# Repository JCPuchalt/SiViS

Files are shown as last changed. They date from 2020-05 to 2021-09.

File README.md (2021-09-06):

# SiViS
New methods for C. elegans assays lifespan automation have been evaluated, these are for improving C. elegans deteccion, and these are described in research article [1].
In addition, other methods are used for vision system inspection [2] and for c-elegans detection [3], all of these are evaluated.

### Research article [1]
[1] Puchalt JC, Sánchez-Salmerón AJ, Ivorra E, Llopis S, Martínez R, Martorell P. Small flexible automated system for monitoring Caenorhabditis elegans lifespan based on active vision and image processing techniques. Sci Rep. 2021 Jun 10;11(1):12289. doi: 10.1038/s41598-021-91898-6. PMID: 34112931; PMCID: PMC8192789.

### Research article [2]
[2] Puchalt JC, Sánchez-Salmerón AJ, Martorell Guerola P, Genovés Martínez S (2019) Active backlight for automating visual monitoring: An analysis of a lighting control technique for Caenorhabditis elegans cultured on standard Petri plates. PLOS ONE 14(4): e0215548. https://doi.org/10.1371/journal.pone.0215548

### Research article [3]
[3] Puchalt, J.C., Sánchez-Salmerón, A., Ivorra, E. et al. Improving lifespan automation for Caenorhabditis elegans by using image processing and a post-processing adaptive data filter. Sci Rep 10, 8729 (2020). https://doi.org/10.1038/s41598-020-65619-4

#### Example assemby and code on [2]
* It is described in document https://github.com/JCPuchalt/c-elegans_smartLight

#### Example code on [3]
* It is described in document https://github.com/AntonioJoseSanchezSalmeron/lifespan

#### Hardware description on [1]
In this repository are the .stl files to print in 3D printer. 
* bridge.stl
* door.stl
* filter.stl
* lid.stl
* pre_rack.stl
* rack.stl
* electronicBox.stl
* displayBox.stl
* frame.stl
* bolt.stl

Then assemby vibration system and adjust to vision system as follow 
https://github.com/JCPuchalt/SiViS/blob/master/AssemblyManual.pdf

#### Pallet assembly
These are the parts:
* pallet_rigidPart.stl
* pallet_middlePart.stl
* pallet_flexiblePart.stl

Assembly the pallet part as follow https://github.com/JCPuchalt/SiViS/blob/master/AssemblyPallet.pdf

## The Code
You shall download this repository on Ubuntu 18.04 machine in the folder you wish. 
Once download, open a terminal and set in the SiViS folder.
1. CaptureCE_App:
   Then follow the README.md file of Code/CaptureCE_App folder.
2. ProcessorCE_App:
   Then follow the README.md file of Code/ProcessorCE_App folder.
3. SiViS_App:
   Then follow the README.md file of Code/SiViS_App folder.

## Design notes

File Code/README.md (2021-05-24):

## The code
There are three pieces of software.

* SiViS_App (Running on Raspberry Pi)
* CaptureCE_App (Running on Desktop Computer)
* ProcessorCE_App (Running on Desktop Computer)

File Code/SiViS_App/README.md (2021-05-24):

## SiViS_App
This code is downloaded and installed on Rasperry Pi 4. 
It may be useful to consult previous documentation in https://github.com/JCPuchalt/c-elegans_smartLight.

### Hardware description
Components:
* Raspberry Pi 4
* Pi NoIR Camera V1
* 7" Raspberry Pi Display
* Raspberry power supply (at least 2Amp)
* Micro SD card (at least 16GB)

The camera should be coplanar to the display focusing at the center of it at a distance of about 8cm.
The camera and the display must be firmly grasped, since any minimum displacement will decalibrate 
the camera-display correspondences.

### Easy software installation
* Install raspbian on Raspberry Pi 4. 
    1. Download raspbian installer (NOOBS) from https://www.raspberrypi.org/downloads/noobs/
    2. Unzip the downloaded files
    3. Format a Micro SD with FAT32
    4. Copy the unzipped files into the formatted Micro SD.
    5. Place Micro SD into Micro SD card slot of Raspberry Pi.
    6. Connect to Ethernet.
    7. Connect power supply and follow the raspbian installation instructions indicated on display.
    8. Write down the Raspberry Pi IP address. To find it, on a terminal type: 
        `ifconfig` 
* From Raspberry Pi open a Terminal. 
    1. Copy the SiViS\_App folder into (i.e.) [/home/pi].       
    2. Launch file set\_up\_whole\_system.sh and follow instructions. On terminal, set file folder (for example: /home/pi/SiViS\_App) 
        ````
        cd /home/pi/SiViS_App
        chmod +x set_up_whole_system.sh
        sh ./set_up_whole_system.sh
        ````

## Software installation details of set_up_whole_system.sh. It will install and set:

* Download and install OpenCV 3.0 and opencv_contrib
* Download and install userland in [/home/pi/userland] 
(https://github.com/raspberrypi/userland)
* Set GPU memory at 256MB
* Temporarily increase the swap
* Free some memory
* Install libncurses5-dev libncursesw5-dev
* Install git
* Enable SSH
* Enable camera
* Disable camera led
* Download and install SiViS\_App program. Copy code in a folder [/home/pi/]
    ````
    cd SiViS_App
    cmake .
    make
    ````

## Run code on Raspberry Pi
Connect from PC to Raspberry Pi through SSH (on Windows with PuTTY (https://www.ssh.com/ssh/putty/download) or Linux with terminal `ssh pi@Raspberry_IP_Adrees`). That terminal is connected to Raspberry, so type on that terminal:
````
cd SiViS_App
sudo ./c-elegans
````

## Notes

* Make sure that the calibration pattern is captured completely with the camera.
To move it you can modify it with the file "./calibracio/p1.xml".

* Some libraries such as WiringPi may be required for compilation, but they are not required for the application

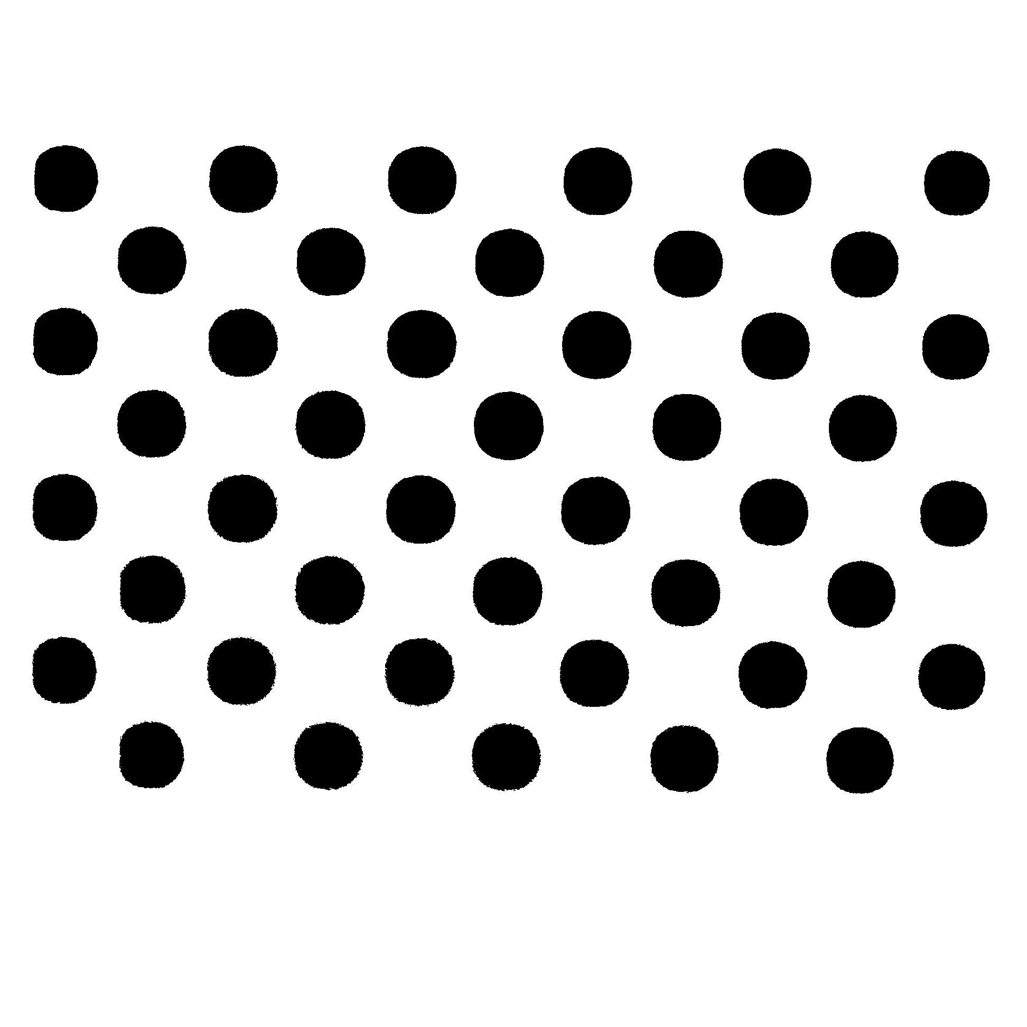
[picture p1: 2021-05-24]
Code/SiViS_App/Patern21.bmp

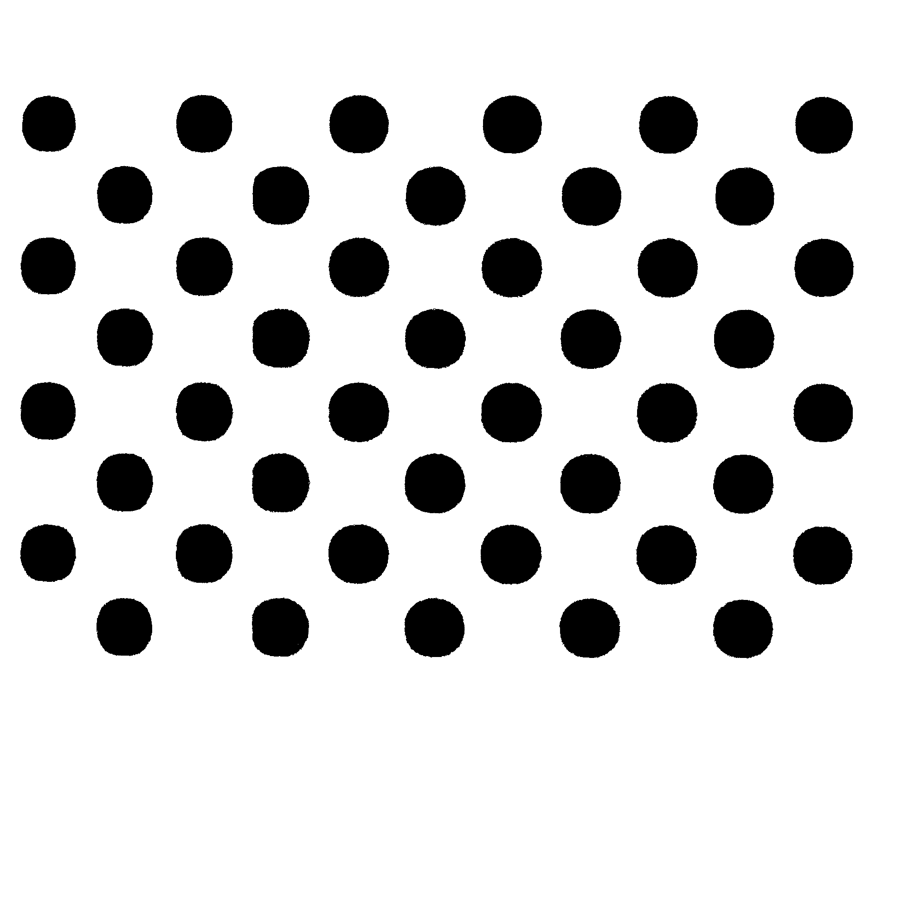
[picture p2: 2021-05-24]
Code/SiViS_App/Patern11.bmp

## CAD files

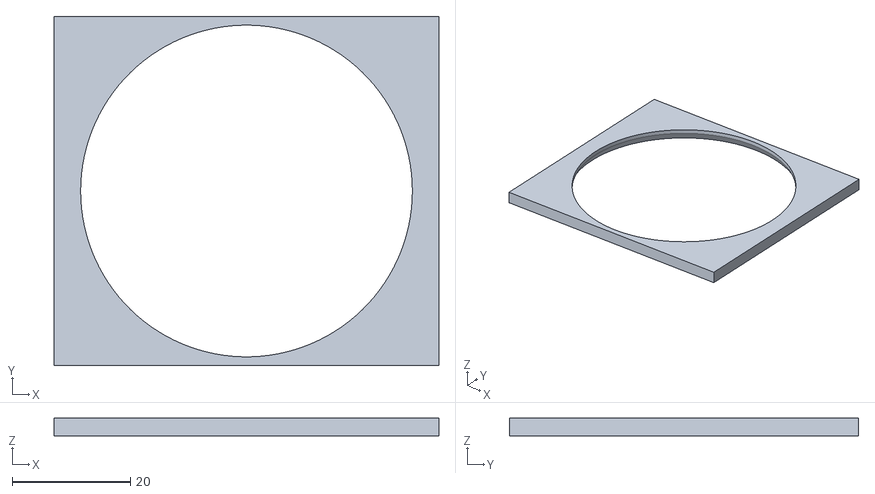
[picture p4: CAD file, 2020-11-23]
Pallet assembly/pallet_flexiblePart.stl
65.0 x 59.0 x 3.00

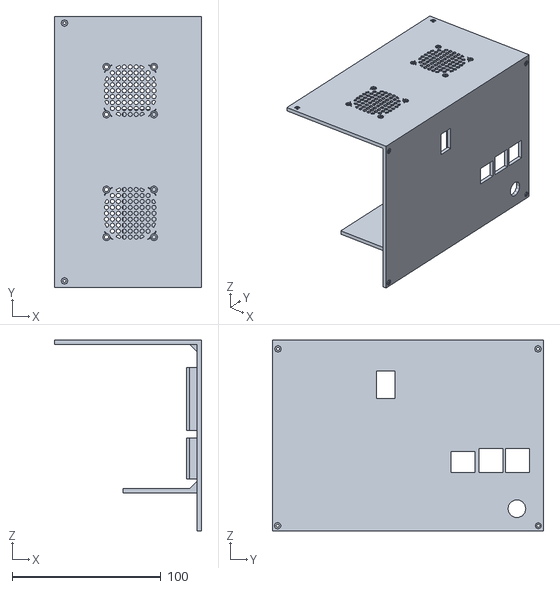
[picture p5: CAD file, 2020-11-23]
assembly parts/lid.stl
99.0 x 182.6 x 128.6

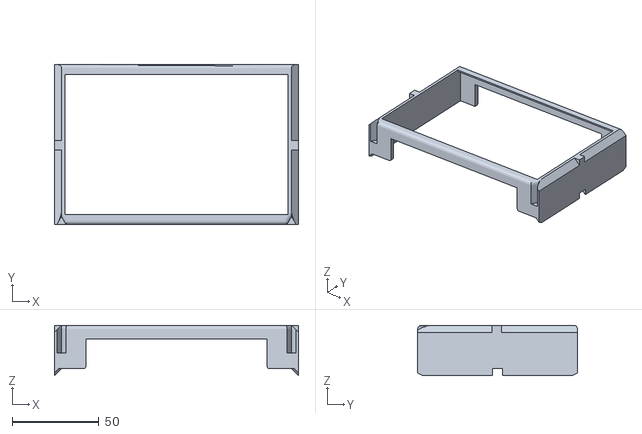
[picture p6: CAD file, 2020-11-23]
Pallet assembly/pallet_rigidPart.stl
140.5 x 92.0 x 29.0

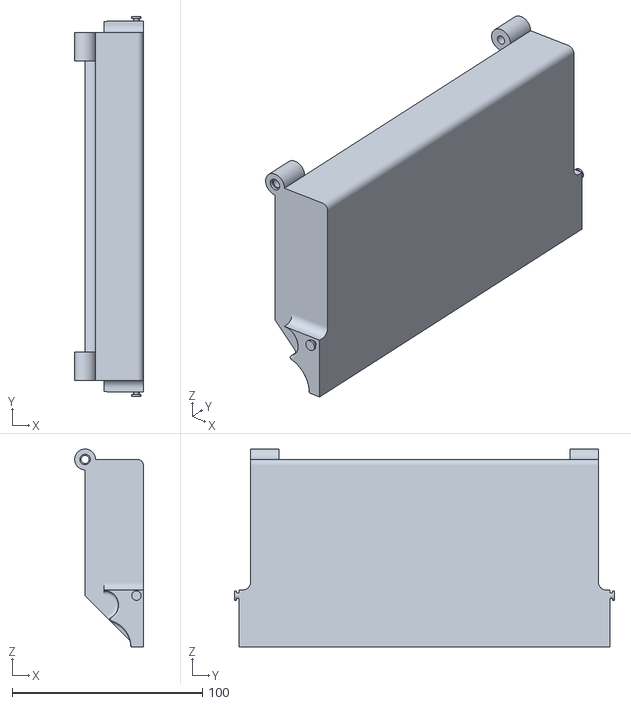
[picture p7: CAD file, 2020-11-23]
assembly parts/door.stl
36.1 x 199.9 x 104.1

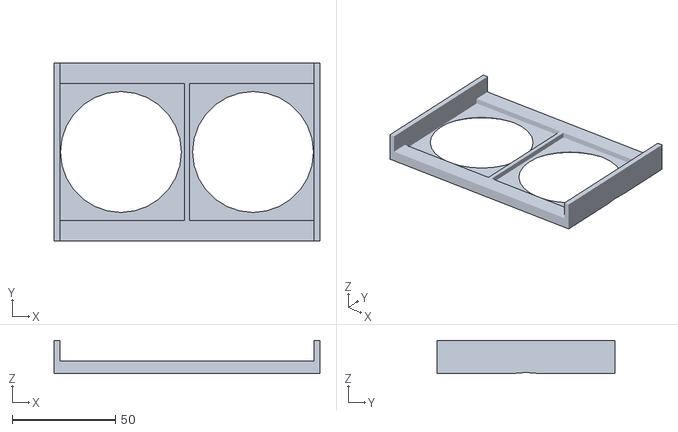
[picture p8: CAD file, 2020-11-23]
Pallet assembly/pallet_middlePart.stl
128.7 x 86.0 x 16.0

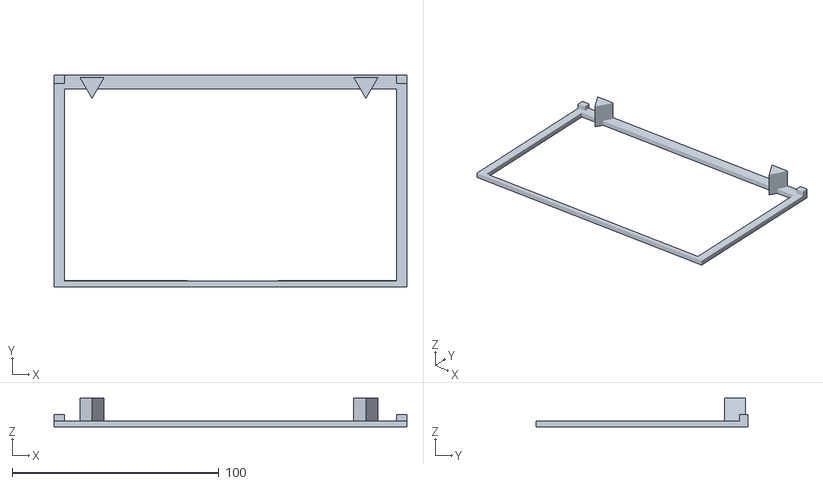
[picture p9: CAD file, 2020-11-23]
assembly parts/frame.stl
170.8 x 102.5 x 14.0

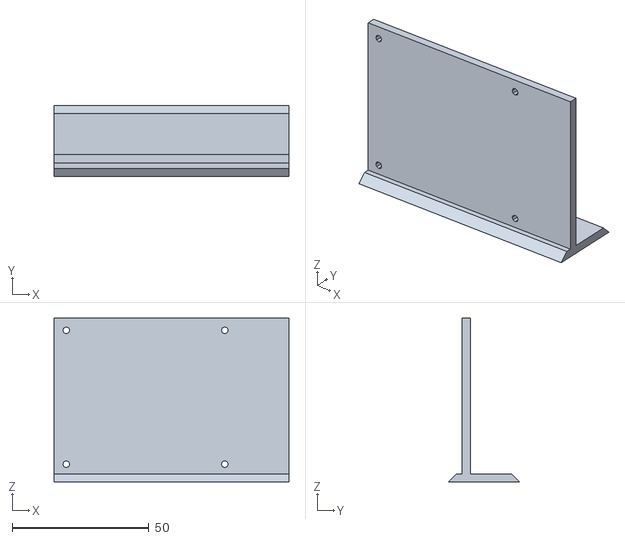
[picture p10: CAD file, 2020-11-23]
assembly parts/rack.stl
86.0 x 26.0 x 60.0

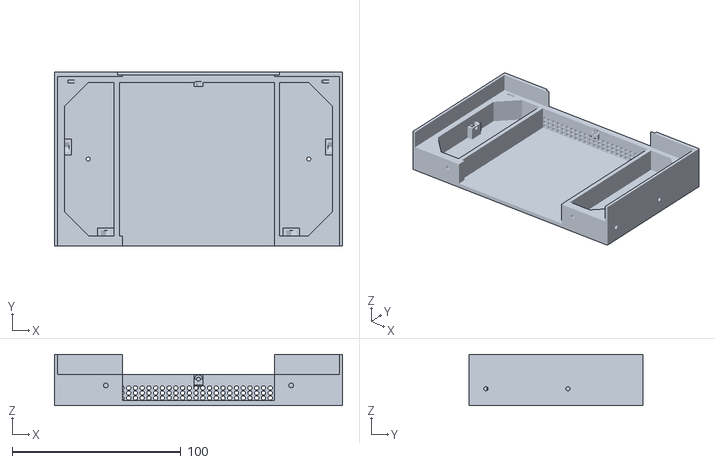
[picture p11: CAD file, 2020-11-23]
assembly parts/displayBox.stl
170.9 x 103.1 x 30.4

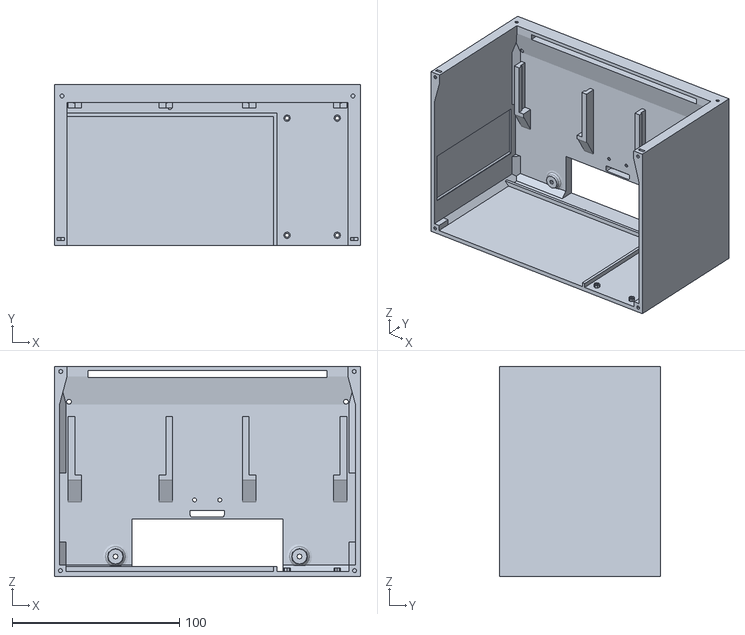
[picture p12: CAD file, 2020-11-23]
assembly parts/electronicBox.stl
182.9 x 96.0 x 125.6

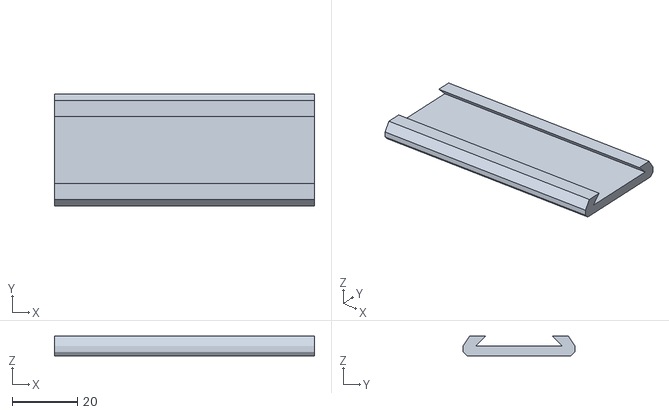
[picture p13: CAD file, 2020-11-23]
assembly parts/pre_rack.stl
80.0 x 34.5 x 6.00

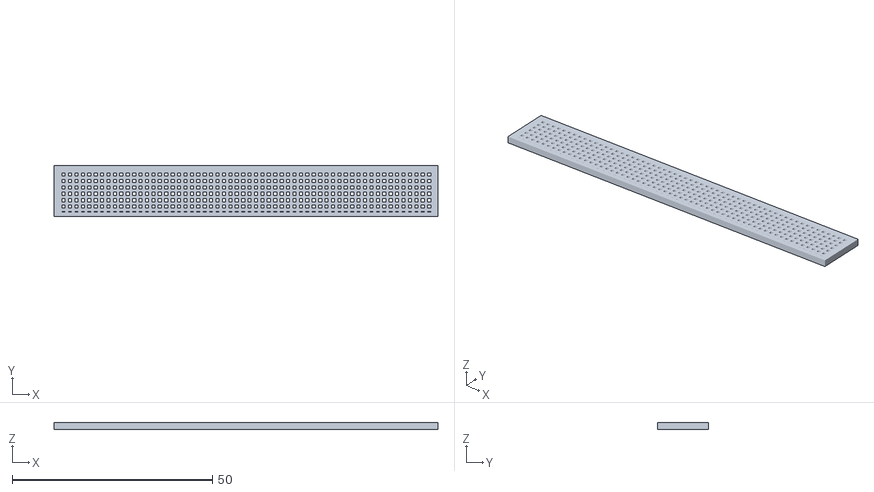
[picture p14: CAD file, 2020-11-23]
assembly parts/filter.stl
95.8 x 12.8 x 1.70

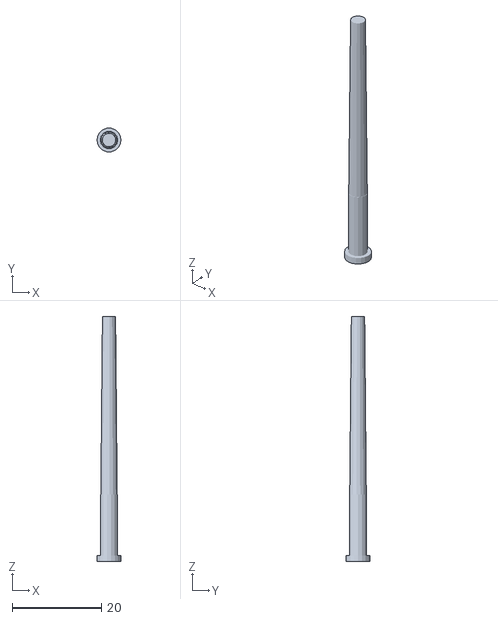
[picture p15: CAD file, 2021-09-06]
assembly parts/bolt.stl
5.40 x 5.32 x 55.0

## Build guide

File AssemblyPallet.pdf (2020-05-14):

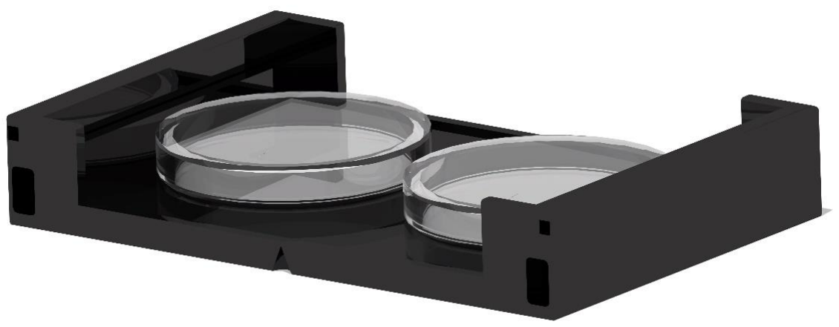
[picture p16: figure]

Joan Carles Puchalt · Antonio Sánchez · Eugenio Iborra · Roberto Martínez · Salvador Genovés · Patricia Martorell

### 1 SiViS assemby manual

# SiViS

## Prototype V1.1

# ASSEMBLY MANUAL

# Pallet

### These are the parts:

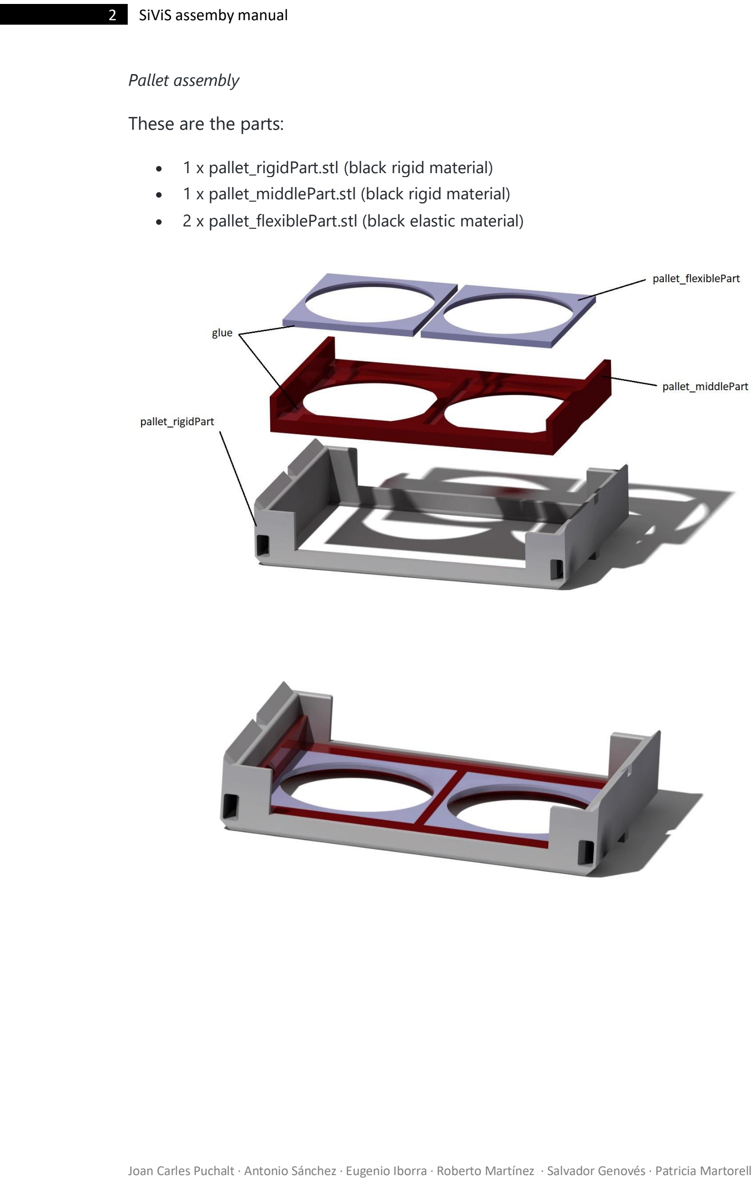
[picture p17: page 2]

Joan Carles Puchalt · Antonio Sánchez · Eugenio Iborra · Roberto Martínez · Salvador Genovés · Patricia Martorell

### 2 SiViS assemby manual

Pallet assembly

- 1 x pallet_rigidPart.stl (black rigid material)
- 1 x pallet_middlePart.stl (black rigid material)
- 2 x pallet_flexiblePart.stl (black elastic material)

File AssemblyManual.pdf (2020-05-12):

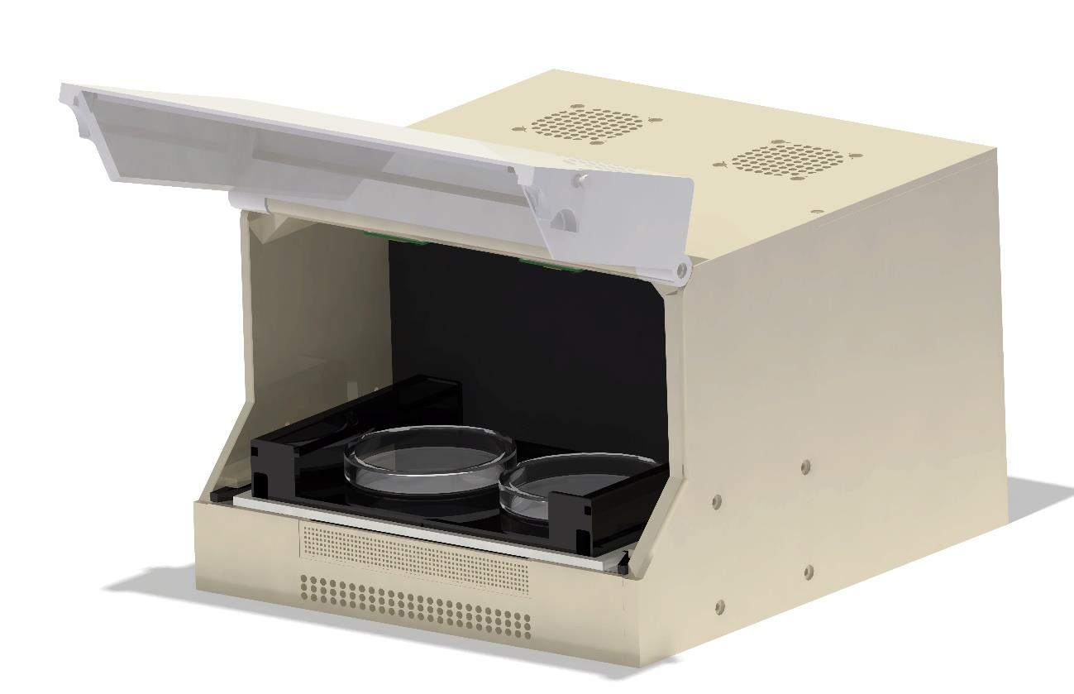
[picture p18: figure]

Joan Carles Puchalt · Antonio Sánchez · Eugenio Iborra · Roberto Martínez · Salvador Genovés · Patricia Martorell

1 SiViS assemby manual

# SiViS

## Prototype V1.1

# ASSEMBLY MANUAL

# PROTOTYPE V1.1

INTRODUCTION

This manual purpose is to help the successfully SiViS assembly, that is, a device created to capture images of C. elegans in a controlled environment.

At first, we (the authors) are going to supply a list of components, describing precisely each component with the aid of figures. Besides, we are going to include also the material features for every component, and an assembly diagram. The parts are jointed together with bolts and screws and, in some cases, glue.

COMPONENT LIST

The component list needed in order to assemble this device is the following:

- Bridge (x1) – Plastic PLA (Polylactic Acid)
- Door (x1) – Plastic PLA (Polylactic Acid)
- Filter (x1) – Plastic PLA (Polylactic Acid)
- Lid (x1) – Plastic PLA (Polylactic Acid)
- Pre-rack (x1) – Plastic PLA (Polylactic Acid)
- Rack (x1) – Plastic PLA (Polylactic Acid)
- Electronic box (x1) – Plastic PLA (Polylactic Acid)
- Display Box (x1) – Plastic PLA (Polylactic Acid)
- Frame (x1) – Plastic PLA (Polylactic Acid)

We employ bolts, screws and glue to assemble, so we provide the following list:

- Plastic bolts (2 units). PLA printed
- Screw M2x12 (8 units). Steel
- Screw M2x10 (6 units). Steel
- Screw M2.5x30 (2units). Steel
- Screw M2.5x20 (6 units). Steel
- Screw M3x30 (4 units). Steel
- Glue (silicone-based)

We too need the electronics parts, which are the following:

- 1 Camera Multiplexer IVPORT Rev.3
- 1 Flat Ribbon Cable 10 cm (FRC100)
- 3 Flat Ribbon Cable 20 cm (FRC200)
- 2 Camera Raspberry Pi
- 1 Raspberry Pi 7” display

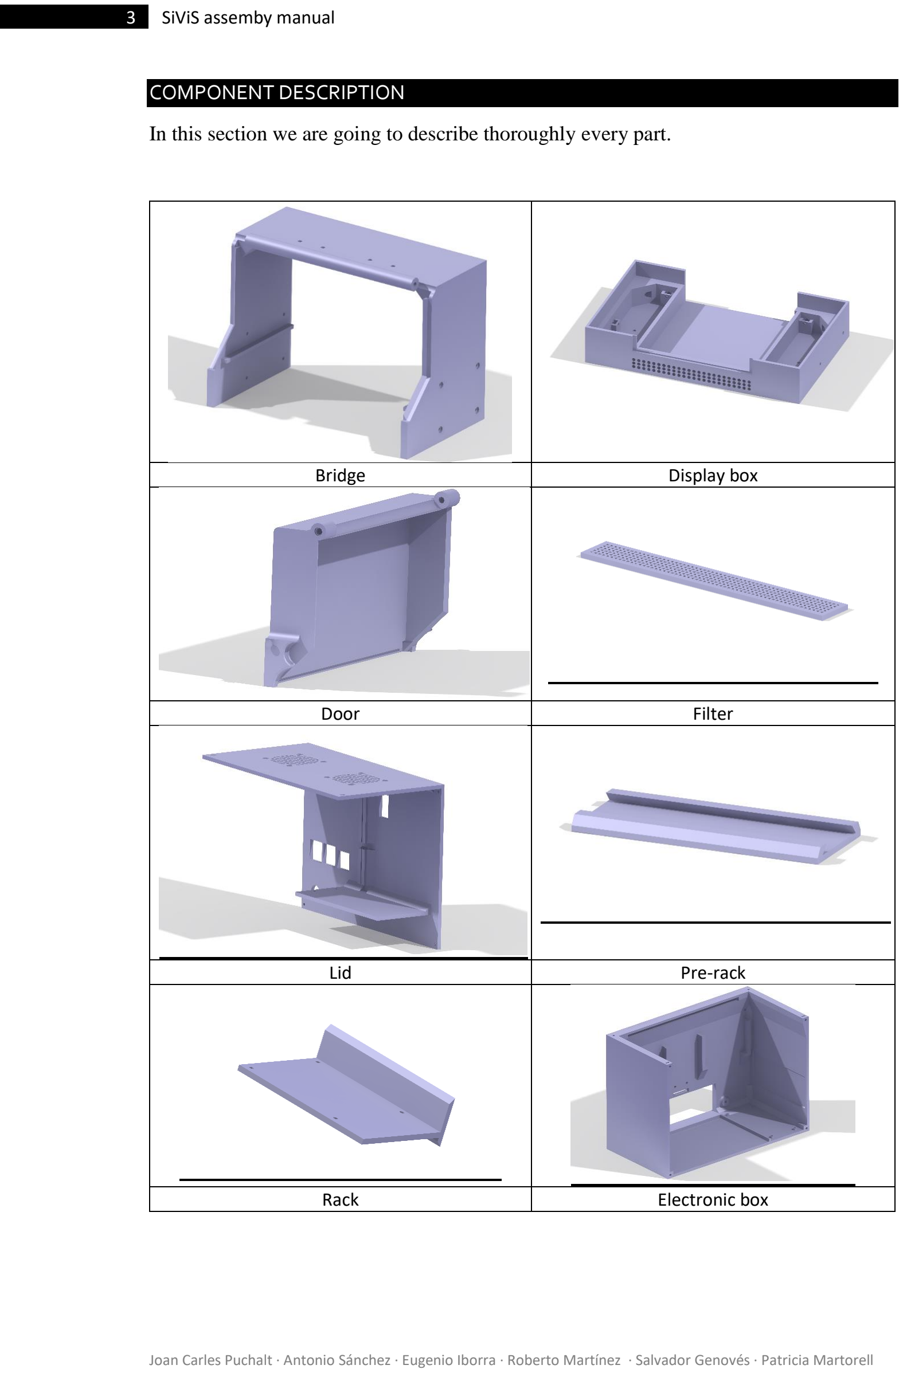
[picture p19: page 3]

COMPONENT DESCRIPTION

In this section we are going to describe thoroughly every part.

Bridge | Display box
Door | Filter
Lid | Pre-rack
Rack | Electronic box

Bridge:

This piece is enough rigid to avoid deformations, where the two cameras are fixed on the top. The door is fixed in the bridge axis with two bolts. On the bottom ‘display box’ is placed.

Display box:

Into this box is placed the display (lighting system), it has holes to allow air flowing. In this piece, the ‘Filter’ is pasted with glue in the slot to avoid dirt.

Door:

This piece purpose is to allow the expert to replace the Petri plates, while avoiding that the plates will be exposed to external light.

Filter:

This is a small part; its purpose is to filter the external air to avoid dust pollution of the plates while these are inside the device and let in air to refrigerate the display.

Lid:

This piece protects the electronic parts of the device from external dust and strikes. This part has two hole patterns in one of its sides, where we need to fasten two fans in order to force air flowing to dissipate the heat generate by the electronic components. It has wireways printed on lid.

Pre-rack:

This is a piece that is glued to the wall of the ‘Electronic box’. It is a prismatic piece, with a dovetail to assemble with the rack (the rack fixes the Raspberry Pi).

Rack:

This piece is where we install a Raspberry Pi.

Electronic box:

This is the piece that we fasten to the back of the bridge piece, where all the electronics are installed. The tree parts (display box, bridge and electronic box) have pipes between them to allow crossing the air flow.

Frame:

This part is to hold the pallet, where Petri plates are placed, thus Petri plates are always at the same position.

UNION METHODS

Here we provide a list of the needed screws to mount the device:

- Plastic bolts (2 units).PLA
- Screw M2x12 (8 units). Steel
- Screw M2x10 (6 units). Steel
- Screw M2.5x30 (2units). Steel
- Screw M2.5x20 (6 units). Steel
- Screw M3x30 (4 units). Steel
- Glue (silicone-based)

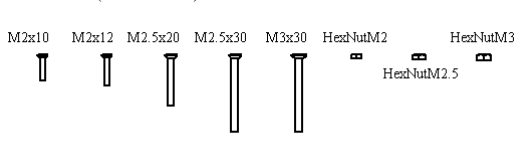
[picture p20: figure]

Plastic bolts:
These bolts are made of Polylactic Acid plastic. We made them via additive

ELECTRONICS COMPONENTS

In this section we describe the electronic components needed in order to the SIVIS device to work properly. The list is the following:

Camera Multiplexer IVPORT Rev.3:

This electronic part’s function is to connect the Flat Ribbon Cable to multiplex the signal received from the camera’s controller (A raspberry Pi). It is a red PBC with four outputs and one input. Here is a photo of this PCB:

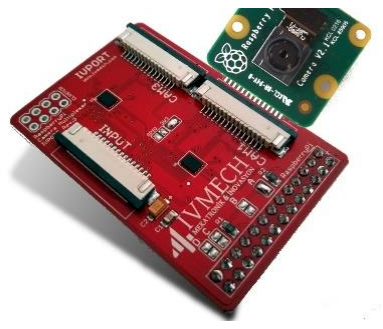
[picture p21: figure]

Multiplexer

Flat Ribbon Cable 10 cm and 20 cm:

It is printed circuitry in a flexible plastic matrix to transfer data between electronic devices.

Camera Raspberry Pi:

That camera is fastened to the ‘Bridge’ piece, where it goes on the inside ceiling of that piece. It is really a little PCB with a mini camera welded on top with tin wire.

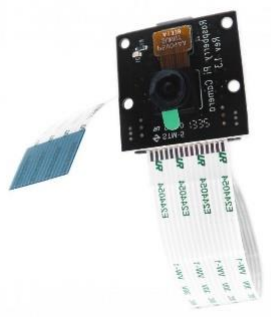
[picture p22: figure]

The Raspberry Pi Camera

We need two units of that electronic device. These are fastened to the inside ceiling of the ‘Bridge’ piece with screws.

ASSEMBLY SCHEME

## Preparing the pieces:

1. Remove excess material from each plastic component carefully.
2. Paste the filter on the front side of the display box.
3. Paste the rubber vibrator on the frame vibrator.
4. Place and paste the pre-rack on one side of the electronic box.
5. Place the nuts in its places (nut holes) and fix with glue. Be careful not to occlude the inner part of the hole.
a. Metric 2mm nuts.
b. Metric 2.5mm nuts.
c. Metric 3mm nuts.
6. Cut the EVA rubber, cover and paste to the inspection inner.
7. Remove touchscreen from display. Touchscreen is fixed with thermal glue, which to weaken it must be heated to 70 degrees during five minutes.
8. Connect the driver to the display.
9. Install the wiring in the ‘Lid’ piece.
a. Place the fans and screw to the lid.
b. Place the switch in the lid.
c. Place the power connector.
d. Follow the electric scheme.

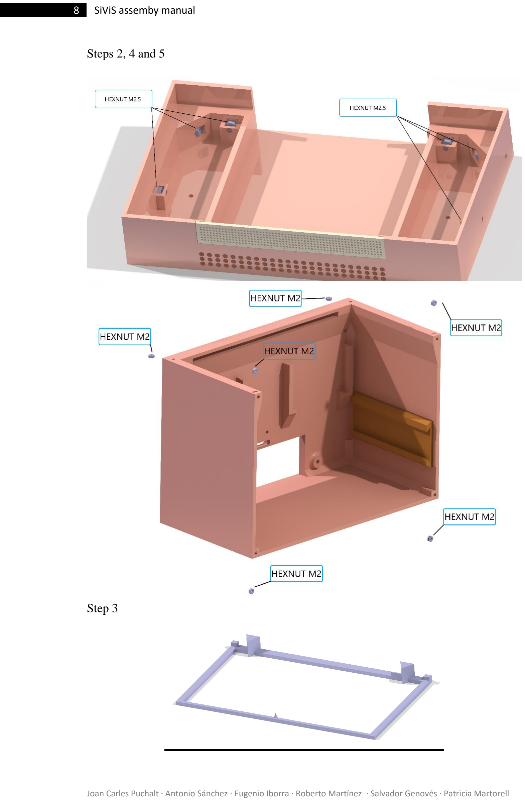
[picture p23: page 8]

Steps 2, 4 and 5

Step 3

## Assembly:

10. Place the cameras in its position and screw them to the ‘Bridge’ piece.
11. Place the display in the display box and place the diffuser on display.
12. Place the frame vibrator on the diffuser.
13. Screw the bridge and the display box between them.
14. Pass the camera cables and the display cable through the slots to electronic box
15. Screw the electronic box to the bridge and to the display box.
16. Screw the Raspberry Pi to the rack and place the rack in the pre-rack slot.
17. Connect the cables.
a. Connect the camera cables to the multiplexer.
b. Connect the input multiplexer to the camera slot in Raspberry Pi.
c. Connect the Dupont cable of multiplexor to GPIO.
d. Connect the display cable to the camera slot of Raspberry Pi.
e. Connect the Dupont cable of display supply to the Raspberry Pi GPIO.
f. Connect the Dupont cable supply to the Raspberry GPIO.
18. Place the lid and screw it to the electronic box.
19. Place the door and introduce the two bolts in their holes.

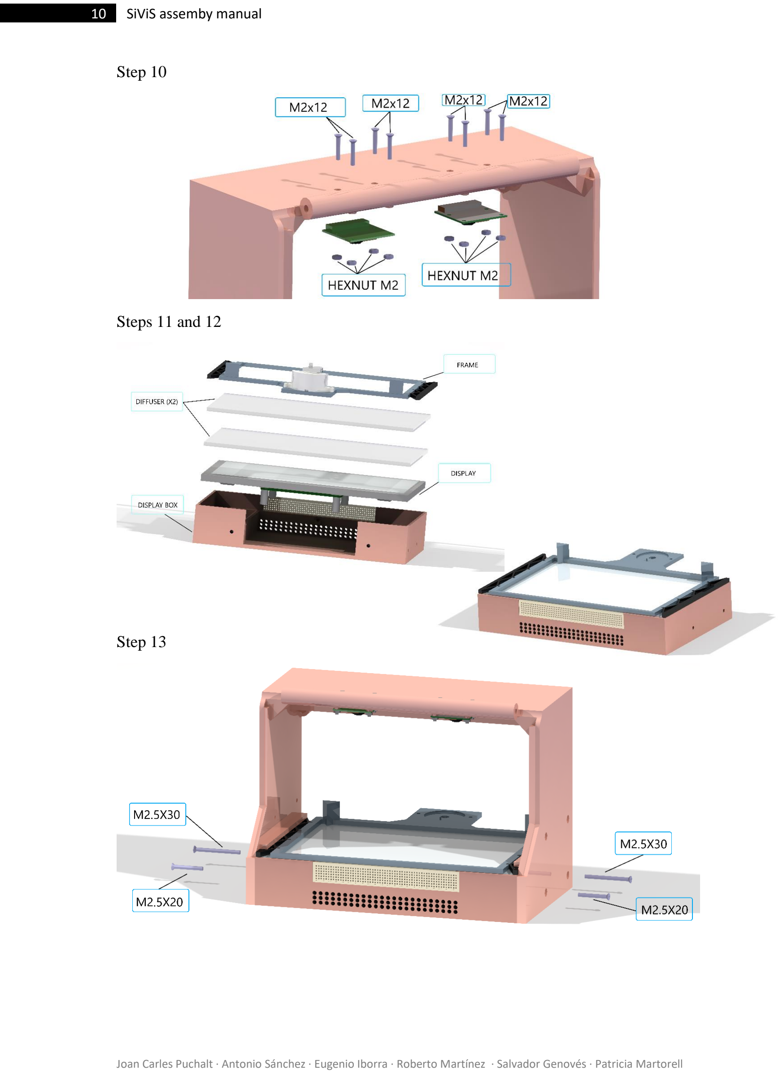
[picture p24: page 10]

Step 10

Steps 11 and 12

Step 13

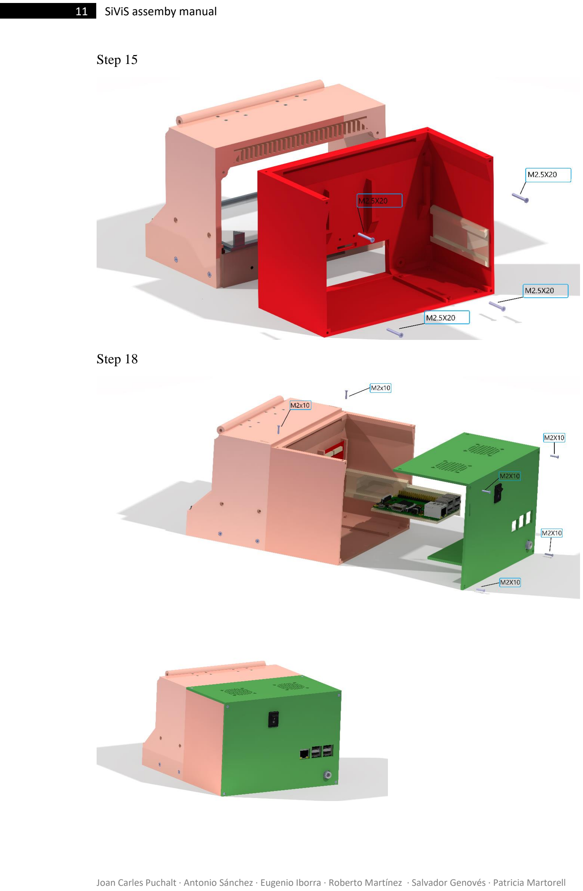
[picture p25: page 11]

Step 15
Step 18

Step 19

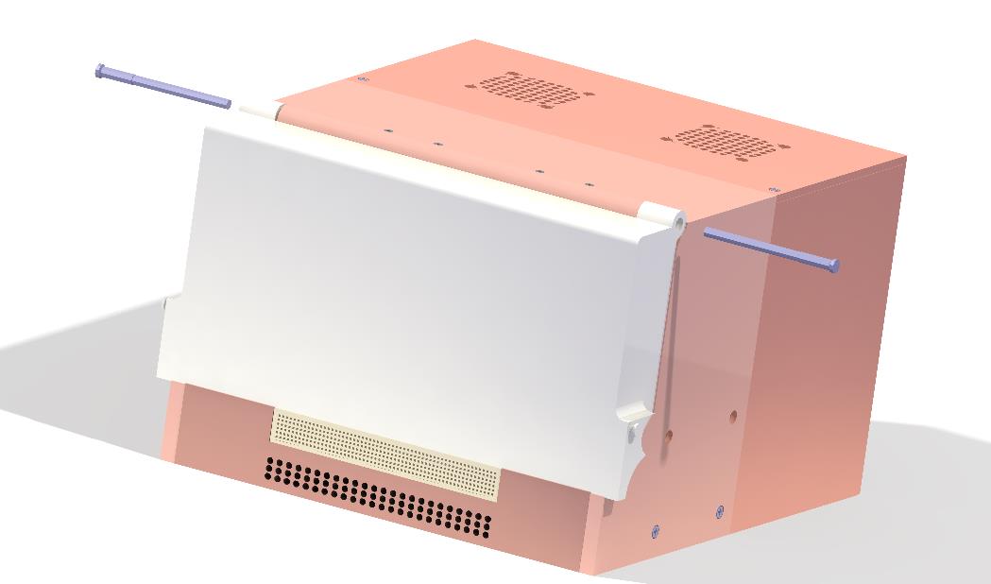
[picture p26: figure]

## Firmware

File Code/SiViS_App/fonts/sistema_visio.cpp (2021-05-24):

#pragma once

#include "../llibreries/llibreries.hpp"
#include "../llibreries/sistema_visio.hpp"

#ifdef _DEBUG    
#pragma comment(lib, "opencv_core246d.lib")     
#pragma comment(lib, "opencv_imgproc246d.lib")   //MAT processing    
#pragma comment(lib, "opencv_highgui246d.lib")    
#pragma comment(lib, "opencv_stitching246d.lib");  
  
#else    
#pragma comment(lib, "opencv_core246.lib")    
#pragma comment(lib, "opencv_imgproc246.lib")    
#pragma comment(lib, "opencv_highgui246.lib")    
#pragma comment(lib, "opencv_stitching246.lib");  
#endif  

using namespace cv;
using namespace std;



/***************************************************************************************
Constructuor de Clase: "sistema_visio". Inicio de clase. Crea, inicializa... variables
****************************************************************************************/
sistema_visio::sistema_visio(int id, int conf, int num_cam, int configPort[], Display* disp, int cicles, int IP_Port)
{
	con_conexion=false; conectat=false;   proyecte_nou=false;    bloquejat=false;
	G_Local=true;       enviar=false;     capturando=false;      inici_local=false;
	inici_remot=false;  iniciat=false;    proyecto_creado=false; abortar=false;
	fin_captura=false;  apagar_RPI=false; 

	foto=false;
	compensada=true;
	monoCamara = false;

	//fusionada	= (unsigned char*) malloc (sizeof(char)      * WIDTH_FRAME*HEIGHT_FRAME*4);

	numMuestras=30;
	estat_enviament = 8; //LLIURE;
	Port_IP = IP_Port;

	idSV=id;
	config=conf;
	display=disp;
	num_camaras = num_cam;
	CICLES=cicles;

	strcpy(ruta_tablaCalibracionFusion    	, "./configuracio/tablaCalibracionFusion");
	crear_ruta_tablaCalibracionFusion();

	strcpy(ruta_tablaInterseccion    	, "./configuracio/tablaInterseccion");
	crear_ruta_tablaInterseccion();

	strcpy(ruta_idCAMARA    		, "./configuracio/idCAMARA");
	crear_ruta_idCAMARA();

	buffer = new bufferCircular();

	ImagenDisplayVector  = display->pImagenDisplayVector();
	ImagenDisplayTextura = display->pImagenDisplayTextura();

	codicImage=0;
	memcpy(numPort, configPort, 4*sizeof(int));

	imagen   = (unsigned char*) malloc (sizeof(char) * WIDTH_FRAME * HEIGHT_FRAME * num_cam);
	evaluado = (unsigned char*) malloc (sizeof(char) * WIDTH_FRAME * HEIGHT_FRAME * num_cam);
	memset ( evaluado, 0, sizeof(char) * WIDTH_FRAME * HEIGHT_FRAME * num_cam );


	tabla_calibracionFusionInversa = (long int*) malloc (sizeof(long int) * WIDTH_FRAME * HEIGHT_FRAME * num_cam * 2);
	memset ( tabla_calibracionFusionInversa, 0, sizeof(long int) * WIDTH_FRAME * HEIGHT_FRAME * num_cam * 2);


	idCAMARA = (unsigned char*) malloc (sizeof(char) * WIDTH_FRAME * HEIGHT_FRAME * num_cam * 2);
	memset ( idCAMARA, 0, sizeof(char) * WIDTH_FRAME * HEIGHT_FRAME * num_cam * 2);


	tabla_Interseccion = (int*) malloc ( sizeof(int) * WIDTH_PANT * HEIGHT_PANT * num_cam );
	memset ( tabla_Interseccion, 0, sizeof(int) * WIDTH_PANT * HEIGHT_PANT * num_cam );

	NUEVA_TABLA = (int*) malloc ( sizeof(int) * (int)floor(WIDTH_FRAME * HEIGHT_FRAME*0.3) );
	memset(NUEVA_TABLA, 0, sizeof(int) * (int)floor(WIDTH_FRAME * HEIGHT_FRAME*0.3) );


	detectadaInterseccion = (unsigned char*) malloc ( sizeof(char) * WIDTH_PANT * HEIGHT_PANT * num_cam * 4);
	memset ( detectadaInterseccion, 0, sizeof(char) * WIDTH_PANT * HEIGHT_PANT * num_cam * 4);


	//detectada = (unsigned char*) malloc ( sizeof(char) * WIDTH_PANT * HEIGHT_PANT * num_cam * 4);
	//memset ( detectada, 0, sizeof(char) * WIDTH_PANT * HEIGHT_PANT * num_cam * 4);


	// Definir ports del Multiplexor
			//pin  7,11,12
	int portMUX[4][3]={   {0, 0, 1},   //PORT CAM1
			      {1, 0, 1},   //PORT CAM2
			      {0, 1, 0},   //PORT CAM3
			      {1, 1, 0} }; //PORT CAM4


	// Crear Camares
	//CAM = new camara[num_camaras](1);
	CAM = reinterpret_cast<camara *>(new char[num_camaras * sizeof(camara)]);
	for (int i = 0; i < num_camaras; i++) {
    		new(&CAM[i]) camara(i+1, num_camaras, this);
	}


	// Si es Sistema de Vision Principal Se creará un hilo de conexión tipo servidor para
	// recibir las calibraciones
	if( SV_Principal ) {
		pthread_create(&conexion_id, NULL, crear_Servidor_SistemaVison_Master, this );
	}

	
	bool _AUTONOMO=false;


	// Configurar Camares
	for (int i=0; i<num_camaras; i++)
	{	
		int nPort = numPort[i];

		//CAM[i].SetId(i+1);
		CAM[i].setDisplay(display);
		CAM[i].pEvaluado(evaluado);
		CAM[i].pDetectarInterseccion(detectadaInterseccion);
		CAM[i].setCaracteristicas(num_cam, idSV, nPort, config);
		CAM[i].setPort ( portMUX[nPort-1][0], portMUX[nPort-1][1], portMUX[nPort-1][2]);
		CAM[i].crear_ruta_homografia();
		CAM[i].crear_ruta_patron();
		CAM[i].crear_ruta_tablaCalibracion();
		CAM[i].crear_ruta_homografiaPlanoPlaca();
		CAM[i].crear_ruta_tablaInterseccion();
		CAM[i].loadPatron();
	}


	// Calibraciones (hay dos tipos: Local y Remota)

	// Calibraciones Locales
	for (int i=0; i<num_camaras; i++)
	{
		if(1) //!_AUTONOMO
		{
			if ( CAM[i].GetId() == idCam_Ppal ||  withMUX)
			{
				cout << "calibracio local..." << CAM[i].GetId() << endl;
				if( CAM[i].CE_Calibrar() )
				{
					cout << "Calibrada cámara local: " << i+1 << endl << endl;
					CAM[i].enviaAlMaster();
					//-----parla=true;
				}
			}
		}
	}

	// Calibraciones Remotas.
	for ( int i=0; i<num_camaras; i++ )
	{
		if ( !withMUX ) // SV_Secundario &&  //CAM[i].GetId() != idCam_Ppal && !withMUX)
		{
			cout << "calibracio remota cámara: " << CAM[i].GetId() << endl;
			//CAM[i].solicitarDibuixarPatro();
			CAM[i].preparadaComunicar(true);
			// ---------------------------
			CAM[i].loadHomographyInverseParams();
			CAM[i].loadHomographyNivelPlaca();
			// ---------------------------
			while( !CAM[i].isMatrizCalibracionRecibida() && !CAM[i].isMatrizCalibracionEnviada() )
			{
				CAM[i].enviaAlMaster();
				display->dibuixar();
				usleep(100000);
			}
			CAM[i].CE_CalibrarRemoto();
		}
	}
	cout << "Calibraciones remotas realizadas" << endl;
	display->colorDisplay(0,0,0,255);
	display->dibuixar();

	if( Cantitat_Camares>1 ) {
		if(1) //!_AUTONOMO)
		{
			detectarInterseccionesX2();
			//detectarInterseccionesX4();

			// ---------------*****************----------------------------------------
			cout << "NO GUSTAR" << endl;
			memset ( detectadaInterseccion, 0, sizeof(char) * WIDTH_PANT * HEIGHT_PANT * 2 * 4);
			//if( (calibrada && recalibrar) || !existeArchivo )
			{
				for (int i=0; i<num_camaras; i++)
				{
					CAM[i].Calculo_Tabla_Calibracion();
					CAM[i].Init_Textura();
				}

				cout << "Creando tabla para los pixeles de interseccion" << endl;
				calculoPixelesIntersectados();
			}
		}


		/*
		// Comprobar si tiene que Calibrar
		int calibra = 0;
		for (int i=0; i<num_camaras; i++)
			calibra+=(int)(!CAM[i].ExisteTabla())+(int)CAM[i].isRecalibrada();

		*/
		// Calcula la tabla 
		//if (calibra)
			calibracioDeFussio();
		//else
		

	
		//if(!recalibrar) || _AUTONOMO
		{
			for (int i=0; i<num_camaras; i++)
			{
				CAM[i].loadTablaCalibracion();
				// Tabla interseccion por cada cámara
				CAM[i].load_TablaInterseccion();
			}
			loadTablaInterseccion();
			loadTablaFusionInversa();
		}
	}
	else { // Si solo hay una cámara por Sistema de visión
		for (int i=0; i<num_camaras; i++)
		{
			bool UNAimagen=true;
			CAM[i].Calculo_Tabla_Calibracion(UNAimagen);
		}
	}

	crearFils();

	cout << "Constructor Sistema Visión: Hecho" << endl;

}


void sistema_visio::crearFils (void)
{
	// Crear Una conexio al Servidor. Per a cada Sistema de Visio
	//fils* fil = new fils();
	//fil->StartInternalThread(this);

	// Crear un thread para guardar las imágenes
	pthread_create(&grabar_id, NULL, CE_Guardar, this );
}


/*********************************************************
Proceso
**********************************************************/
void sistema_visio::proceso(void)
{

	display->dibuixar();
	
	foto=false;
	if(ch == 'f') {
		foto=true;
		ch='a';
		cout << "fottttttttttttttttttttttttooooooooooooooooo" << endl;
	}

//	inicialisarCaptura();
//	sincronisacio();
	
	if(Cantitat_Camares==1) {
		// Compensacio Rapida de les camares locals ()
		for (int iC=0; iC < num_camaras; iC++)
		{
			if ( CAM[iC].GetId() == idCam_Ppal ||  withMUX)
			{
				// Compensación rápida
				if( !CAM[iC].found_min() ) {
					CAM[iC].CE_Compensar_Rapido();
					//CAM[iC].saveTexturaCompensada();
					//saveTexturaInterseccion();
					codicImage=0;
				}
			}
		}
	}

	struct timespec t0 = Inicia_Temporisador();
	for (int iC=0; iC < num_camaras; iC++)
	{
		// Procesa si la Cámara es Local o si Se utiliza MUX
		if ( CAM[iC].GetId() == idCam_Ppal ||  withMUX)
		{
			// Captura
			bool unaCaptura = false;
			CAM[iC].CE_Capturar (unaCaptura);
			// FIN Captura


			if( Cantitat_Camares>1 ) { // Si el Sistema de Visio te mes d'una Camara

				// Compensaciones
				// Compensaciones del Display
				if ( withMUX ) {  
					if( !CAM[iC].found_min() ) {
						CAM[iC].CE_Compensar_Rapido();
						codicImage=0;
					}
				}
				if ( !withMUX ) {
					CAM[iC].CE_Compensar();
				}

				// Comprimir Interseccion de la Textura para enviar al Master
				CAM[iC].compresionImagenInterseccion();
				// Orden para enviar Textura e Intersección al Master
				CAM[iC].enviaAlMaster();
				// FIN compensaciones


				// Fusiona la imagen de 1 cámara
				CAM[iC].fussioParcial( imagen, foto );
				// Comprime la imagen intersectada de 1 cámara
				CAM[iC].fussioInterseccioParcial(imagen);

				struct timespec t1 = Inicia_Temporisador();

				if(SV_Principal) {
					// Procesa la Intersección si es SV Principal
					procesarInterseccionParcial (foto);
					// Añade, comprime y envía a la Fusionada la Intersección
					CAM[iC].enviarInterseccioReconstruida( imagen, anticTamanyTabla );
				}

				cout << "Temps deteccio: "<< Medix_temps(t1) << endl;
				// Orden para enviar los resultados de fusión
				if(SV_Secundario) {
					CAM[iC].enviaAl_SV_Principal();
				}
				// FIN fusiones

			}
			else { // Si el Sistema de Visio te nomes una Camara
				// Compensaciones del Display
				if ( withMUX ) {  
					if( !CAM[iC].found_min() ) {
						CAM[iC].CE_Compensar_Rapido();
						codicImage=0;
					}
				}
				imagen = CAM[iC].Get_Vect_Im();
			}


			//cout << CAM[iC].Calcular_Luz_Media() << endl;
			CAM[iC].CE_Error_Compensacion();
			//CAM[iC].CE_Compensar_Rapido();

		}
	}
	int estat = Get_Estat_Enviament();
	//CAM[0].enviarImage();
	//cout << "estat -> " << estat << endl;
	//cout << "Temps bucle: "<< Medix_temps(t0) << endl;

	// -------------
	int numCamLocals = 0, estadoCapturando=0;
	for (int iC=0; iC < num_camaras; iC++)
	{
		if ( CAM[iC].GetId() == idCam_Ppal ||  withMUX)
		{
			estadoCapturando += CAM[iC].getCapturando();
			numCamLocals++;
		}
	}
	//cout << "numCamLocals: " << numCamLocals << ", estadoCapturando: " << estadoCapturando << endl;
	if ( estadoCapturando == numCamLocals ) {
		capturando=true;
		codicImage++;
	} else {
		capturando=false;
		codicImage=0;
	}


//	compensacionInterseccion();

	/*
	* Funciones de fusion
	*/
	//fussio_imagens();
	// Fusiona en una imagen única
//	fussioInversa_imagens();
	// Realiza la fusión de la imagen de manera parcial en dos imágenes diferentes
//	fussioInversa_imagensIndividual();


	// Genera ruta de imagen a grabar para modo autonomo
	int totalBytes = 2592*2592;
	char direccionDeGrabacion[150]="";
	//generadorDeRuta( direccionDeGrabacion );

	// Añadir al buffer para guardar en Memoria
	//buffer->addImage( imagen, direccionDeGrabacion, totalBytes );
	//Sum_It_Imagens();

}
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

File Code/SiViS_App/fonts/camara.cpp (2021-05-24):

#pragma once

#include "../llibreries/llibreries.hpp"
#include "../llibreries/camara.hpp"


#ifdef _DEBUG    
#pragma comment(lib, "opencv_core246d.lib")     
#pragma comment(lib, "opencv_imgproc246d.lib")   //MAT processing    
#pragma comment(lib, "opencv_highgui246d.lib")    
#pragma comment(lib, "opencv_stitching246d.lib");  
  
#else    
#pragma comment(lib, "opencv_core246.lib")    
#pragma comment(lib, "opencv_imgproc246.lib")    
#pragma comment(lib, "opencv_highgui246.lib")    
#pragma comment(lib, "opencv_stitching246.lib");  
#endif  

using namespace cv;
using namespace std;

/** Histograma de Referencia **/
double H_Referencia[256]={0};


float puntos_pantalla[90][2]=
{
			     {0, 0}, {42*1*texelRatio, 7*42},	{0, 0}, {42*3*texelRatio, 7*42}, 	{0, 0}, {42*5*texelRatio,  7*42},   {0, 0},  {42*7*texelRatio,  7*42},   {0, 0},  {42*9*texelRatio,   7*42},   {0, 0},
	{0, 42*6}, 	     {0, 0}, {42*2*texelRatio, 6*42}, 	{0, 0}, {42*4*texelRatio, 6*42}, 	{0, 0}, {42*6*texelRatio,  6*42},   {0, 0},  {42*8*texelRatio,  6*42},   {0, 0},  {42*10*texelRatio,  6*42},
	
			     {0, 0}, {42*1*texelRatio, 5*42},	{0, 0}, {42*3*texelRatio, 5*42},	{0, 0}, {42*5*texelRatio,  5*42},   {0, 0},  {42*7*texelRatio,  5*42},   {0, 0},  {42*9*texelRatio,   5*42},   {0, 0},
	{0, 42*4}, 	     {0, 0}, {42*2*texelRatio, 4*42}, 	{0, 0}, {42*4*texelRatio, 4*42},	{0, 0}, {42*6*texelRatio,  4*42},   {0, 0},  {42*8*texelRatio,  4*42},   {0, 0},  {42*10*texelRatio,  4*42},

			     {0, 0}, {42*1*texelRatio, 3*42}, 	{0, 0}, {42*3*texelRatio, 3*42},	{0, 0}, {42*5*texelRatio,  3*42},   {0, 0},  {42*7*texelRatio,  3*42},   {0, 0},  {42*9*texelRatio,   3*42},   {0, 0},
	{0, 42*2},  	     {0, 0}, {42*2*texelRatio, 2*42},  	{0, 0}, {42*4*texelRatio, 2*42},	{0, 0}, {42*6*texelRatio,  2*42},   {0, 0},  {42*8*texelRatio,  2*42},   {0, 0},  {42*10*texelRatio,  2*42},

			     {0, 0}, {42*1*texelRatio,   42}, 	{0, 0}, {42*3*texelRatio, 1*42},	{0, 0}, {42*5*texelRatio,  1*42},   {0, 0},  {42*7*texelRatio,  1*42}, 	 {0, 0},  {42*9*texelRatio,   1*42},   {0, 0},
	{0,    0}, 	     {0, 0}, {42*2*texelRatio,    0}, 	{0, 0}, {42*4*texelRatio,    0},	{0, 0}, {42*6*texelRatio,     0},   {0, 0},  {42*8*texelRatio,     0},   {0, 0},  {42*10*texelRatio,     0}                     

};


/***************************************************************************************
Constructuor de Clase: "camara". Inicio de clase. Crea, inicializa... variables
****************************************************************************************/
camara::camara( int iD, int numero_camaras, sistema_visio* SiVi )
{
	H_Referencia[43]=0.1;
	H_Referencia[44]=0.3;
	H_Referencia[45]=1.2;
	H_Referencia[46]=5.5;
	H_Referencia[47]=16.5;
	H_Referencia[48]=28.0;
	H_Referencia[49]=25.5;
	H_Referencia[50]=13.8;
	H_Referencia[51]=5.6;
	H_Referencia[52]=1.8;
	H_Referencia[53]=0.5;
	H_Referencia[54]=0.1;

	corregir_x=0; corregir_y=0; CNTA=0;
    	Iteracions_Compensacio = 1;
	minim_error_compensacio = 100.0;
    	MET_Ant=0; mija_error_compensacio=0;
    	It_Erro=0; min_found=false;
    	alpha=0; tamInterseccio=0; tamFusionadaParcial=0;
	errorQuadraticMig_Anterior=0;
	tamInterseccionParcial=0;
	enviaInfoAlMaster=false;
	enviaInfoAlPrincipal=false;
	tablaParcial_Enviada=false;
	num_camaras = numero_camaras;

	bloquejat=false; capturando=false; inici_local=false;
	inici_remot=false; iniciat=false; fin_captura=false;

	compensada=true;
	SV = SiVi; 

	FYmin=0; FYmax=0;
	minimIdx = 10000000;
	maximIdx = 0;
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

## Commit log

2020-05-12 AssemblyManual v1.1
2021-09-06 bolt
    It is need 2 bolts
    [bolt.stl]
